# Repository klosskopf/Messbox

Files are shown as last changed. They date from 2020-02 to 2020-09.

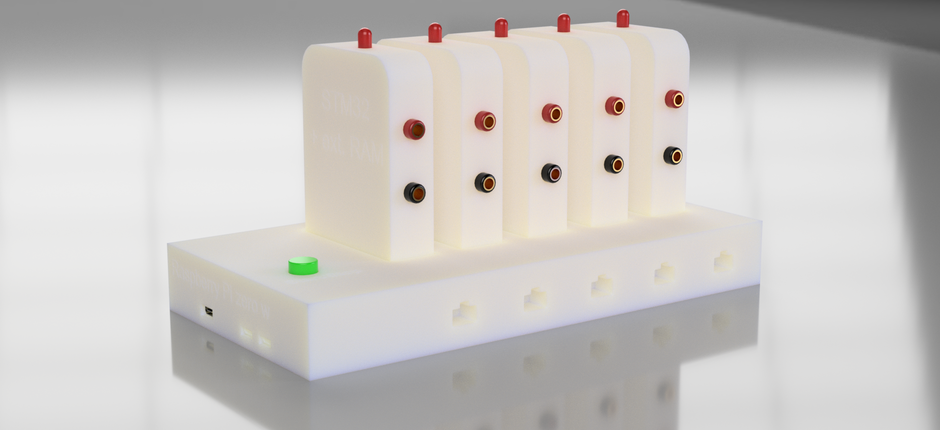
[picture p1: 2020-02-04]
doc/Messbox_Render.png

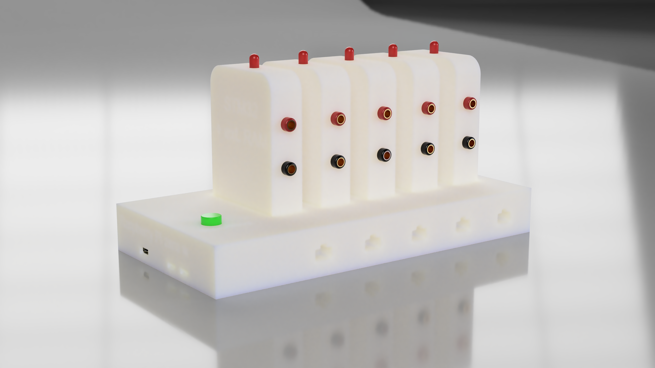
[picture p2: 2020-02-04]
doc/Messbox_Render_2K.png

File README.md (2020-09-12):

Dieses Repository beinhaltet alle Dateien zum Projekt Messbox 2000

Im Ordner *Raspberry* befindet sich der QT 5.11.3 C++ Code für die Middleware und Kennlinienerzeugung
Die Software muss mit root-Rechten ausgeführt werden. Damit die Aplikation ein Gui anzeigen kann,  
muss ```export XAUTHORITY=/home/pi/.Xauthority``` an /etc/profiles angehängt werden.

Im Ordner *Basisplatine* findet sich der Schaltplan und Layout für die Basisplatine

Im Ordner *STM32* befindet sich der C Code für die STM32 uC

Im Ordner *Steckkarte* befindet sich der Schaltplan und Layout für die Steckkarte.

Im Ordner *ATMEGA88* befindet sich der C Code für den atmega88 zur Erzeugung der sample frequenz und allgemeines

Im Ordner *BOM* finden sich Stücklisten und Bestellungsinfos für JLCPCB

Im Ordner *doc* finden sich alle Schemata, die das System beschreiben

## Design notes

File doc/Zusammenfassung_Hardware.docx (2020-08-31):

# Basisplatine-Hardware

Die Basisplatine übernimmt im Wesentlichen die Aufgaben eines Mainboards. Sie dient als Verbindungsglied zwischen Raspberry Pi und den einzelnen Steckkarten. Sie versorgt die Elemente mit allen nötigen Resourcen, wie 5V und 3,3V Spannungsversorgung und dem synchronen Sampletakt, der von einem Atmega88 Mikrocontroller erzeugt wird.

## Spannungsversorgung

Um einen möglichst großen Eingangsspannungsbereich nutzen zu können, besteht die erste Stufe der Spannungswandler-Schaltung aus einem Buck-Converter, der Spannungen zwischen 6V und 25V effizient auf 5V wandelt. Somit kann der Nutzer sich frei für eine Spannungsquelle entscheiden, solange diese mindestens 5W liefern kann. Denkbar sind beispielsweise 9V, 12V oder 15V Netzteile, aber auch mobile Lösungen, wie 2S, 3S, oder 4S Li-Ion Akkus, sollte die Betriebsdauer des integrierten Akkus nicht ausreichen. Wenn eine externe Spannungsversorgung angeschlossen ist, wird der interne Akku mit ca. 0,5A geladen. Verbaut ist eine 18650 Li-Ion Zelle mit 2000mAh. Mit dieser Zelle kann die Messbox bis zu einer Stunde ohne externe Stromversorgung betrieben werden. Um im Netzbetrieb den Akku laden zu können, wird das System in diesem Fall ganz über die bisher erzeugten 5V betrieben und nicht über die Batteriespannung. Gelöst wird dies durch zwei als OR verschaltete Shotkey –Dioden. Um die, um die Diodenspannung gesunkene, Spannung beziehungsweise die Batteriespannung wieder auf die benötigten 5V zu bekommen, folgt nun noch ein Boost-Converter. Um etwaige Rippel/Spitzen aus dem Rest der Schaltung zu halten, folgt nun noch ein LC-Filter. Mit diesen 5V werden der RaspberryPi und die Steckkarten versorgt, die nach der galvanischen Trennung daraus selbst 3,3V für die CMOS basierte Logik zu erzeugen. Auch der Raspberry selbst benötigt eigentlich 3,3V für seinen SOC, diese werden jedoch auf dem Einplatinenrechner selbst erzeugt. Diese werden auch durch den GPIO-Header in die Baisplatine eingespeist und versorgen hier den ATMEGA88. Der AVR könnte zwar auch mit 5V betrieben werden, durch die 3,3V sparen wir uns jedoch die sonst nötigen Pegelwandler für den SPI-Bus. Obwohl die Steckkarten sich ihre 3,3V selbst erzeugen, bekommen diese auch die 3,3V des Raspberry Pi. Damit wird jedoch lediglich das Chip-Select-Signal mit einem Pull-Up versorgt.

## SPI-Bus

Die Kommunikation des Raspberry-Pi mit den Steckkarten und dem ATMEGA88 erfolgt über einen einzigen SPI-Bus. Dieser befindet sich in einer Multi-Slave Konfiguration. Der Raspberry kann frei entscheiden, an wen er alles gleichzeitig Daten schicken möchte. In diesem Fall gibt es Pakete, die an alle Slaves, nur einen Karte, oder nur den ATMEGA88 gehen. Sinniger Weise darf immer nur ein Slave antworten. Um bei der Kommunikation mit mehreren Slaves keinen Kurzschluss zu verursachen, sind die MISO-Signale als open-drain Konfiguriert, wobei sich ein gemeinsamer Pull-Up auf der Basisplatine befindet. Weil ein SPI-Bus sehr empfindlich auf Übersprechen der Datenleitungen auf den Takt reagiert, wurde hierauf besonderes Augenmerk gelegt. Zum einen ist der SPI-Takt getrennt von anderen Datenleitungen gelayoutet und durch Masseflächen Abgeschirmt. Zum anderen sind alle Signale mit 100Ohm Serienterminiert und auf ca. 100Ohm Impedanz dimensioniert.

## ATMEGA88

Die Hauptaufgabe des ATMEGA88 besteht darin, einen exakten Sampletakt bereitzustellen. Dazu teilt dieser einen 12MHz Quarztakt durch einen Peripherie-Timer herunter und gibt das erzeugte Signal direkt in Hardware auch aus. Die Software des ATMEGA88 dient lediglich als Slave am SPI-Bus und konfiguriert die Hardware. Da dadurch noch genügend Resourcen auf dem Mikrocontroller frei sind, übernimmt dieser zusätzlich noch die Kontrolle der Spannungsversorgung. Die gesammelten Daten können über ein GET_STATUS Paket abgefragt werden, finden in der Software jedoch noch keine Verwendung.

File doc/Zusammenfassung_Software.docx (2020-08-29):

# Benutzeroberfläche

Um die Entwicklung und Bedienung so einfach wie möglich zu gestalten, finden sich alle Bedienelemente und der Graph auf einer Oberfläche, die bei Start des Systems gestartet wird.

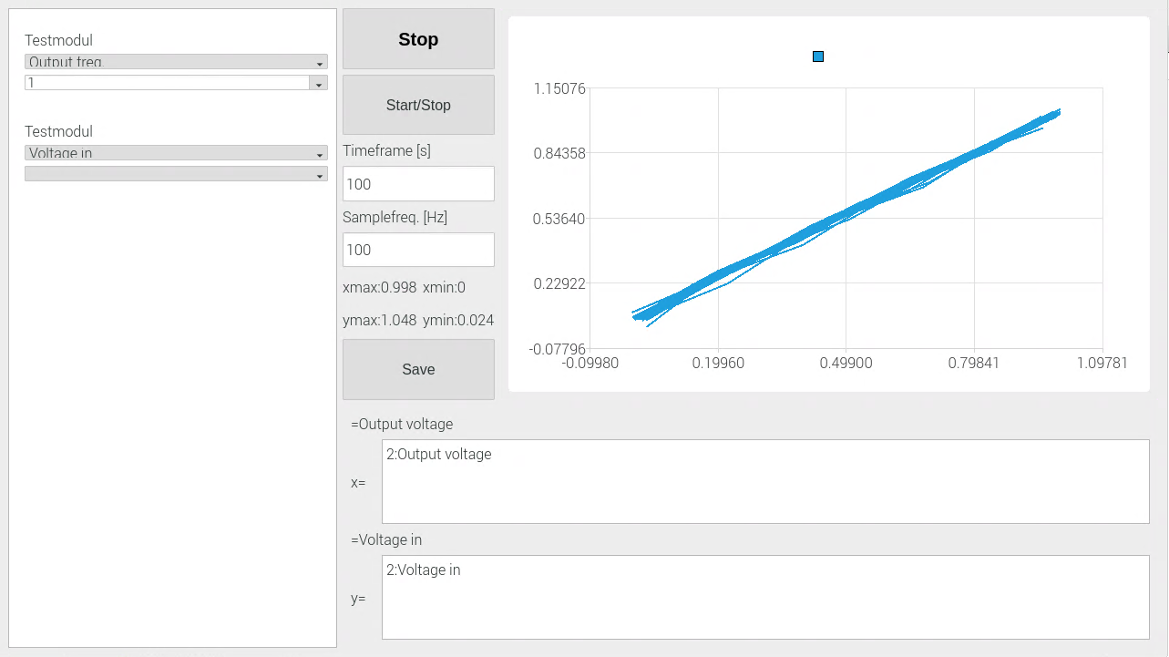
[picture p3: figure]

Die einzelnen Elemente Skalieren mit unterschiedlichen Monitorauflösungen in gleichem Umfang, benötigen allerdings eine Mindestauflösung von 405 x 543 Pixel, wobei die Oberfläche dann nur noch sehr eingeschränkt nutzbar ist. Im linken Abschnitt werden die eingesteckten Karten angezeigt. Schwebt die Maus über einer Karte, wird der Slot angezeigt, den die Karte belegt. Die Zählweise beginnt bei 1 im Slot ganz links. Die RJ45 Buchsen erhalten die Nummern 6-10. Eine dargestellte Karte besteht aus dem Kartennamen, einer Auswahlbox, die die einzelnen Parameter der Karte beinhaltet und einer Werte-Auswahlbox. Wird ein Parameter ausgewählt, wird das Werte-Dropdown Menü angepasst. Je nachdem, ob der Parameter frei anpassbar ist, nur aus einer Liste ausgewählt werden kann, oder gar nicht geändert werden kann. Im obigen Fall besitzt das erste Testmodul einen Parameter “Output freq.“, der frei änderbar ist. Zusätzlich kann aber auch aus einer Liste ein vorgeschlagener Wert übernommen werden. Beim zweiten Testmodul ist der Parameter „Voltage in“ ausgewählt. Dieser Parameter kann nicht geändert werden, sondern dient lediglich als Datenlieferant. Die Karte übermittelt zu Beginn ihren Namen und alle Parameter an die Basisstation. Unter anderem auch die Schreib-Rechte und Wahlmöglichkeiten der einzelnen Parameter.

In der Mitte finden sich die Kontrollelemente. Der erste Button ist eine Kopie des physischen Buttons. Mit diesem kann eine Messung gestartet und gestoppt werden. Findet gerade eine Messung statt, wird „misst…“ angezeigt, ansonsten „Stop“.
Mit dem zweiten Button wird der Messmodus gewechselt. Verfügbar sind „Start/Stop“, in dem eine feste Zeit lang gemessen wird, und „Cont.“, wohinter der Kontinuierliche Mess-Modus steckt. Wird der Modus während einer Messung gewechselt so werden alle bisherigen Werte verworfen und die Messung neu gestartet.
Die Zeitdauer, die im Graph angezeigt wird, kann im Feld „Timeframe“ stufenlos eingestellt werden. Im Start/Stop-Modus entspricht diese der Messdauer. Auch die Sample-Frequenz kann stufenlos eingestellt werden. Hardwarelimitiert sind dabei Werte zwischen 0.1Hz bis 10kHz wählbar, wobei alles über 1kHz aufgrund fehlender Zuverlässigkeit vermieden werden sollte.
Weil es zuweilen recht mühsam ist, Werte aus dem Graphen auszulesen, werden zumindest die aktuellen Minimal und Maximalwerte des sichtbaren Graphen für beide Achsen angezeigt.
Mit dem „Save“-Button können alle erfassten Parameter des Messsystems in „.csv“-Dateien gespeichert werden. In diesem Prozess wird zunächst die aktuelle Messung gestoppt und dann alle Parameter aller Karten restlos ausgelesen. Abhängig von der Anzahl an Karten, Parameter und Messdauer kann das eine Weile in Anspruch nehmen. Im Anschluss wird der Benutzer aufgefordert einen Speicherort für die Dateien auszuwählen. Dies geschieht in einem Dateiexplorer, sodass auch angeschlossene Speichermedien gewählt werden können, wenn diese ein Linux-Kompatibles Dateisystem besitzen (z.B Fat32). In dem ausgewählten Verzeichnis wird eine Ordnerstruktur erstellet. Gekapselt unter einem Ordner mit dem aktuellen Datum und Uhrzeit wird für jede Karte ein eigener Ordner erstellt, der für die einzelnen Parameter eigene „.csv“-Dateien erstellt. So muss der Nutzer in der Auswertung nicht alle Parameter in Excel laden, sondern kann sich nur die genutzten auswählen. Gespeichert wird für jeden Parameter die Zeit in Sekunden und der Messwert.

Welche Messwerte, wie im Graphen dargestellt werden, wird mit den beiden Formeln dargestellt. Hier können für die x-Achse und y-Achse unabhängig mathematische Formeln angegeben werden. Im dargestellten Bespiel wurde der x-Achse der Spannungsausgang der Testkarte aus Slot 2 zugewiesen und der y-Achse der Spannungseingang derselben Karte. Im Testaufbau wurden lediglich die beiden Bananenbuchsen miteinander verbunden. Zuvor wurde der Spannungsausgang mithilfe der Parameter „Output min.“, „Output max.“ und „Output freq“ so konfiguriert, dass eine Dreieckspannung mit 1Hz zwischen 0V und 1V ausgegeben wird. Da viel Karten denselben Namen haben, in unserem Fall zweimal „Testkarte“, muss ein Parameter über seinen Kartenslot und Parameternamen angesprochen werden. „2:Voltage in“ referenziert also den Parameter „Voltage in“ der Karte in Slot 2. Sollte es diesen Parameter nicht geben, wird eine entsprechende Fehlermeldung ausgegeben. Das manuelle Eingeben der Parameter kann umgangen werden, indem die Karte mit ausgewähltem Parameter per Drag and Drop in den Formeleditor gezogen wird. Parameter können auch mit mathematischen Operatoren miteinander kombiniert werden. Zur Verfügung stehen + - * / ( ) D S.
„D“ bildet dabei die Ableitung einer nachstehenden Klammer und „S“ das Integral. Auch Gleitkommazahlen sind erlaubt. Soll auch die verstrichene Zeit in die Achse mit eingehen, so kann der Operator „T“ verwendet werden.

Die dadurch festgelegte Messreihe wird im Graphen dargestellt. Die Achsen skalieren dabei automatisch mit. Befindet sich die Messung im kontinuierlichen Modus, werden alle Messwerte aus dem festgelegten letzten Zeitraum angezeigt. Der Nutzer ist selbst verantwortlich, das System nicht mit der Menge der anzuzeigenden Messwerte zu überfordern. Ein guter Richtwert sind 1000 Messpunkte. Bei mehr als 10000 Messpunkte droht eine Überlastung der CPU und dem Freeze der Benutzeroberfläche. Im Start/Stop-Modus gibt es diese Limitierung nicht. Hier wird nur eine Auswahl der Messwerte angezeigt, sodass die maximale Anzahl in dieser Messung die 1000 nicht überschreitet. Gespeichert werden in beiden Modi aber alle Messwerte, ob sichtbar oder nicht.

# Aufbau der Raspberry Pi Software

## Threads

Die Software des Raspberry Pis ist darauf ausgelegt, den SPI Bus maximal auszulasten. Es soll vermieden werden, dass der Raspberry Pi keine Daten abfragen kann, und somit den Buffer der Steckkarten unnötig strapaziert, nur weil die Daten gerade ausgewertet werden. Es muss auch verhindert werden, dass das Lesen und Decodieren eines besonders langen Pakets Benutzereingaben verzögert. Die von uns gewählte Lösung besteht aus der Aufteilung in mehrere Threads. Das ermöglicht auch den Wechsel von einem Einkern-Systems, wie dem ursprünglich vorgesehenen Raspberry Pi Zero, auf ein Multicore System, wie den Raspberry Pi, der zusätzlich mit weitaus größerem Arbeitsspeicher ausgestattet ist, was die maximale Aufnahmedauer stark erweitert.

Die Threads laufen je eine Endlosschleife, wobei die Synchronisation durch verschieden Maßnahmen gewährleistet bleibt. Die Software besteht aus folgenden fünf Threads:

## Post-Thread:

Der Postthread ist für die Spi-Kommunikation mit den Steckkarten zuständig. Da diese dauerhaft ausgelastet sein soll, bleibt dieser auch immer aktiv. Seine Aufgabe besteht darin, Pakete aus einer queue zu lesen und entsprechend des Protokolls mit Daten zu füllen. Die eigentliche Low-Level Übertragung wird mittels der wiringPi – Bibliothek durchgeführt. Diese nutzt DMA Transfers, wodurch Rechenzeit für andere Tasks frei wird. Wurde ein Paket fertig gesendet und simultan empfangen, so wird es an den Decoder- Thread weitergeleitet, der dieses nun Zeitunkritisch bearbeiten kann. Um Race-Conditions ausschließen zu können, genügt es, lediglich die Queue und Chip-Select-GPIOs mittels Mutex-Semaphoren zu schützen. Um ein korrektes Abarbeiten der Pakete zu gewährleisten, reicht es, das Abfragen der Queue-Größe, sowie das Entnehmen eines Paketes zu schützen. Die Chip-Select-Leitungen werden zusätzlich vom Control-Thread zur Erkennung von neuen Karten benötigt. Diese müssen also auch mithilfe einer Mutex-Semaphore vor gleichzeitigem Zugriff geschützt werden. Die Suche nach neuen Karten wird lediglich selten und sehr schnell abgearbeitet und fällt daher nicht wirklich ins Gewicht. Manche Pakete, wie GET_DATEN und GET_PARAMETER besitzen keine feste Länge. Diese wird von der Steckkarte vorgegeben und wird in den ersten Bytes übermittelt. Für ein Paket sind in diesem Fall also zwei DMA Transfers notwendig. Der Thread ist in sich in einem Modul geschlossen, und bietet eine API zum Hinzufügen von neuen Paketen.

## Decoder-Thread

Nachdem das Paket empfangen wurde, können die Daten zeit-unkritisch ausgewertet werden. Weil die empfangenen Daten eine zu schützende Ressource darstellen, kann es im decode-Schritt zu Wartezeiten kommen, die die SPI-Kommunikation nicht aufhalten sollen. Aus diesem Grund benötigt auch der Decoder-Thread eine Warteschlange, die vom Postthread gefüllt wird. Hier kann es jedoch zu Zeiten kommen, in denen keine Pakete zum Auswerten bereit sind. In diesen Zeiten soll der Thread nicht ins busy-wait laufen, sondern Schlafen. Die Synchronisation wird hier durch eine condition-variable gelöst, die den Thread nur dann aufweckt, wenn er gerade schläft. Der Decoderer erkennt selbstständig die Art des Pakets und speist die erhaltenen Daten in den Rest des Systems ein.

## Control-Thread:

Gefüttert wird der Post-Thread durch den Control-Thread. Dieser ist in dem control-Modul beheimatet, das zentral den Zustand des Systems leitet. Die Aufgabe des Control-Threads ist es, neue Karten zu finden und nach Parameteren zu fragen, sowie die Daten zu besorgen, die gerade für den Graph benötigt werden. Die Bandbreite des SPI-Buses, limitiert durch das SPI-Modul des STM32, erlaubt es nicht, von allen Karten ständig alle Parameter-Daten abzufragen. Weil die Liste mit momentan gebrauchten Parametern jedoch vor der Grapherstellung geschützt werden muss, ist es sinnvoll, nur für das Befüllen der Post-queue diesen eigenen Thread zu verwenden.

## Graph-Thread:

Der Graphthread ist lediglich ein Relikt aus vergangenen Versuchen, der nun lediglich eine Funktion im Haupt-Thread aktviert, die neue Datenpunkte in den Graph lädt. Diese Funktion soll in einem weiteren Refaktoring-Schritt durch einen QTimer ersetzt werden.

## Haupt-Thread:

Im Hauptthread werden die Qt-Objekte verwaltet. Also die Gui-Elemente. Dazu zählen insbesondere die dynamische Anzeige der Karten, das Parsen der Achsen-Gleichungen und Anzeigen des Graphen. Weil ein Gui Element in Qt nur im Hauptthread erzeugt werden kann, die neue Karte jedoch im Decoder-Thread erzeugt wird, besteht eine Karte aus zwei Objekten. Das eine für den Zugriff auf die Karte mit Parameterliste und einem Gui-Teil. Durch Erzeugen der Karte im Decode-Thread wird ein Signal an den haupt-Thread gesandt, der dann den zugehörigen Gui-Teil erstellt.
Als besonders Leistungshungrig hat sich das Erstellen des Graphen herausgestellt. Ein Graph in Qt besteht aus einem Graph, einem View-Objekt, das die Darstellung übernimmt und Serien, die die Datenpunkte besitzen. Zunächst wurde versucht, einzelne Datenpunkte aus der Serie zu löschen und neue Anzuhängen. Wie sich herausstellte, ist das eine sehr ineffiziente Möglichkeit. Besser ist es, die gesamte Serie mit neuen Datenpunkten zu befüllen (series->replace()). Dabei wird ein Zwischenspeicher benötigt, der gesamt in die Serie übernommen wird. Dazu wird zunächst festgestellt, zu welchem spät möglichsten Zeitpunkt alle Parameter über Daten verfügen. Befindet sich die Messbox im Kontinuierlichen Modus, so werden nun die nicht mehr benötigten Datenpunkte aus dem Zwischenspeicher gelöscht. Und dann neue Datenpunkte bis zum vorher bestimmten Zeitpunkt hinzugefügt. Nun können die Datenpunkte der Serie ausgetauscht werden. Was bleibt ist das Problem, dass die Achsen des Graphs, und damit auch der Anzeigebereich, eingestellt werden muss. Und dazu wird der minimale und maximale Wert des aktuell sichtbaren Bereichs benötigt. Ein stupides Durchgehen des Zwischenspeichers ist jedoch nur bei geringen Datenmengen durchführbar und wird daher auch nur im Kontinuierlichen Modus angewandt. Im Start-Stop-Modus wird beim Hinzufügen des Datenpunkts der minimale und maximale Wert aktualisiert. Weil bei langen Zeitdauern, wie sie spezifiziert sind, die Performance massiv beeinflusst würde, wenn mit jedem Zeitpunkt alle Datenpunkte neu gezeichnet werden würden, werden die angezeigten Datenpunkte in diesem Modus auf 1000 begrenzt. Es werden natürlich auch die dazwischen liegenden, nicht angezeigten Punkte mit abgespeichert.
Festgelegt, welche Parameter auf welcher Achse angezeigt werden, wird durch Auswertung der Achsen-Formeln. Die sich daraus ergebende Struktur wird aktualisiert im Fall einer neuen Eingabe, oder auch bei Einfügen und Ausstecken einer Karte. Die Formeln werden zunächst in die einzelnen Komponenten geparst, um Parameter von Zahlen und Rechenoperationen unterscheiden zu können. In einem weiteren Schritt werden nun die Elemente in die richtige Topologie gebracht. Gelöst wird dies rekursiv durch Prioritäten der einzelnen Elemente. Um den neuesten Zeitpunkt zu erhalten, oder einen Wert für einen Zeitpunkt zu bekommen, muss lediglich die entsprechende Funktion in der Wurzel aufgerufen werden, die dann rekursiv weiterläuft und die Rechenoperationen anwendet. Obwohl die Daten nur in single precision float Qualität erhoben werden, erfolgt die Berechnung und Darstellung im double Zahlenbereich. Das sichert auch bei großen Zahlen die erforderliche Genauigkeit in den Berechnungen.

# Programmablauf

Nun soll beschrieben werden, wie das Programm funktioniert. Das Programm wird ständig versuchen, den Graph zu erstellen. Weil die Datenpunkte des Graphen ja nicht beständig neu gesucht werden, führen bestimmte Aktionen, wie das Eingeben eines neuen Zeitfenster oder Achsenformel zu einem Löschen des Graphen, wodurch dieser einmalig wieder komplett neu erstellt wird. Es ist ersichtlich, dass das Erstellen des Graphen völlig von den anderen Aktivitäten unabhängig ist. Das hat den Nachteil, dass die Daten und der Datenbehälter vor gleichzeitigem Zugriff geschützt werden müssen. Insbesondere muss das Programm davor geschützt werden, Daten von einem Parameter zu erfragen, den es schon gar nicht mehr gibt. Das kann vorkommen, wenn während des Erstellens des Graphen eine Karte ausgesteckt wird, oder sich die Achsenbelegung ändert. Gelöst wurde das Problem durch eine große Mutex-Semaphore, die sowohl die Graph Erstellung, als auch den Achsen-Formel-Parser und das Löschen einer Karte klammert. Da zwei der drei verwendeten Stellen nur sehr selten vom Benutzer ausgeführt werden, ist die Performanceeinbuße hinnehmbar.

Damit der Control-Thread weiß, welche Daten gerade benötigt werden, hält der Parser eine Liste an Parameter-Pointern bereit. Der Control-Thread wird nun beständig versuchen, die queue des Post-Thread mit 10 Paketen gefüllt zu halten. Dadurch können jederzeit Status, Parameter und Befehle gesendet werden und der Rest der SPI-Kapazität wird im Round Robin Verfahren mit Datenanfragen gefüllt. Auch das Abfragen nach Daten ist unabhängig vom Zustand des Systems. Das ermöglicht es, Auch nach abgeschlossener Messung, den Graph mit anderen Parametern zu belegen. Diese werden dann so schnell wie möglich aus dem Zwischenspeicher der Steckkarten ausgelesen. Nachdem der Decoder die Daten ausgelesen hat, stehen sie im System zur Verfügung, bis eine neue Messung gestartet wird. Dann werden die Daten sämtlicher Parameter gelöscht und die Steckkarten setzen ihren Zwischenspeicher zurück. Intern liegen die Datenpunkte in einem vector gespeichert in den Parametern. Das hat den Vorteil zu einer verketteten Liste, dass die Daten auch mit einem Index angesprochen werden können. So muss nicht jedes Mal die gesamte Liste bis zum gesuchten Zeitpunkt abgesucht werden. Stattdessen merkt sich der Parameter den zuletzt verwendeten Index. Es ist nun sehr wahrscheinlich, dass bei erneutem Aufruf derselbe(doppelte Verwendung des Parameters) oder nächste Datenpunkt gesucht wird. Auch wenn Datenpunkte in der Anzeige übersprungen werden, wie es im Start-Stop-Modus der Fall ist, lässt sich so die Graph Erstellung bedeutend beschleunigen.

# Protokoll

Um den Datenaustausch maximal effizient zu gestalten, setzen wir auf unser eigenes Daten und Kommando Protokoll. Die Verwendung einer Einheitlichen JSON – Form wurde zwar in Betracht gezogen, letztendlich wollten wir allerdings die Möglichkeit sowohl float-Daten binär, als auch ascii-Parameter, ohne viel overhead versenden zu können. Die übertragung erfolgt in Little-Endian, da sowohl STM32, als auch Raspberry Pi auf Little-Endian Arm Architekturen bestehen. Das erleichtert die Umwandlung von empfangenen Bytes in float-Variablen ungemein. Es sind bisher 8 Befehle definiert, wobei das Protokoll Platz für 256 bieten würde.

## GET_PARAMETER: 0x01 : An einzelne Karte

Erkennt der Control-Thread eine neue Karte, sendet er ein GET_PARAMETER Paket an den entsprechenden Slot. Mit diesem Paket wird der Name der Karte erfragt und welche Parameter die Karte bietet. Ein Parameter besteht dabei aus einer Nummer, die künftig zur Identifikation im SET_PARAMETER und GET_DATEN Paket dient, einem Parameternamen, mit dem der Benutzer interagiert, minimal und maximal Werten und einer optionalen Werteauswahl. Die einzelnen Angaben sind immer nur durch ein Zeichen getrennt. Die Paket-Länge bezieht sich auf die Byte-Zahl des Parameter-Teils

| Befehl | Paket-Länge | Parameter
MOSI | 0x01
MISO | | 0-20000 | Kartenname,Parameternummer,Name,Typ,Parametrierbar,Min,Max{Wahl1,Wahl2,…}Parameternummer,…

uint8_t uint32_t ascii

Befehl | 0x01 für GET_PARAMETER
Paket-Länge | Byte-Zahl der Parameter
Kartenname | Wird dem Benutzer in der Kartenübersicht angezeigt. Intern verwendet wird jedoch ausschließlich der Index des Slots, in den die Karte gesteckt ist. Es können also auch zwei gleichnamige Karten eingesteckt sein.
Parameternummer | Nummer unter der der Parameter in weiteren Befehlen erreichbar ist
Parametername | Der Name des Parameters wird zusammen mit dem Kartenindex verwendet, um Parameter auf Achsen zuzuweisen
Typ | {s / f} : string oder float. Entscheidet, ob Daten vom Parameter abgefragt werden können und im Graphen dargestellt werden können. String Parameter können zum konfigurieren des Systems genutzt werden.
Parametrierbar | {l /f / n} : Liste, Frei, oder Nicht. Entscheidet, ob und wie der Benutzer den Parameter ändern kann. Liste: Der Benutzer kann keine freien Eingaben machen, aber aus den vorgegebenen Wahlmöglichkeiten wählen. Frei: Der Benutzer kann freie Eingaben machen, die zwischen min und max liegen müssen, sind Wahlmöglichkeiten vorhanden, so werden diese auch als drop down-Menü angezeigt. Nicht: Der Benutzer kann den Parameter nicht verändern. Er dient lediglich als Datenlieferant
Min | Der Minimalwert, der eingestellt werden kann. Muss immer angegeben werden; Wird als ASCII übertragen
Max | Der Maximalwert, der eingestellt werden kann. Muss immer angegeben werden.; Wird als ASCII übertragen
Wahl | Optional: Die Wahlmöglichkeiten, die dem Benutzer angezeigt werden. Werden im geschweiften Klammern angegeben. Falls keine Wahlmöglichkeiten vorhanden sind, folgt der nächste Parameter ohne Klammern mit einem Komma. Alle Wahlmöglichleiten werden als ASCII übertragen.

Wenn die Karte noch nicht bereit ist und nicht antwortet, so wird das Paket im Decoder als Fehlerhaft erkannt und keine neue Karte erstellt. Der Control-Thread wird im nächsten Versuch die Karte wieder als neu erkennen und einen neuen Versuch starten.

## SET_PARAMETER: 0x02 : An einzelne Karte

Ändert einen Parameter in der Karte. Der Parameter wird durch seine Nummer angesprochen. Es werden lediglich ASCII-Werte übertragen. Diese müssen eventuell in der Karte umgewandelt werden. Die Paket-Länge beinhaltet die 4 Byte der Parameternummer und die Länge des ASCII Parameterwert.

| Befehl | Paket-Länge | Parameternummer | Parameterwert
MOSI | 0x02 | 4 - 2^32 | 0 – 2^32
MISO | | | | Parameterwert

uint8_t uint32_t ascii

Befehl | 0x02 für SET_PARAMETER
Paket-Länge | Die Paket-Länge setzt sich zusammen aus 4 + Bytezahl des Parameterwerts
Parameternummer | Eindeutige Zuordnung des Parameters innerhalb der Karte
Parameterwert | Der Wert, auf den der Parameter gesetzt werden soll. Ist immer als ASCII codiert und wird bei Bedarf in der Karte umgewandelt. (atof())

## GET_DATEN: 0x03 : An einzelne Karte

Fordert Daten von einem Parameter an. Um den Bus nicht zu verstopfen und fehlerhafte Pakete ansatzweise zu erkennen, ist die Paketgröße auf 5000 Bytes softwareseitig begrenzt. Es ist ratsam, nur einzelne Pages des Zwischenspeichers auf einmal zu übertragen, um genug Zeit zu haben, neue Daten in das RAM zu laden. Ein Paket besteht dabei aus einer Anfangszeit und fortlaufenden Werten. Die Zeit bezieht sich dabei auf die Samples und nicht die eigentlich vergangene Zeit. Die Umwandlung erfolgt erst bei der Grapherstellung.

| Befehl | Parameternummer | Paket-Länge | Startzeit | Daten
MOSI | 0x03 | 0 - 2^32
MISO | | | 0-5000 | 0-2^32 | Datum1,Datum2,…

uint8_t uint32_t float

Befehl | 0x03 für GET_DATEN
Parameternummer | Damit die Karte angeben kann, wie viele Daten bereit sind, braucht sie den Parameter, um den es geht.
Paket-Länge | Die Paket-Länge entspricht nur der Länge des Daten-Teils. Also Anzahl an Datenpunkten * 4
Startzeit | Die Sample-Zeit des ersten Datums. Folgende Daten erhalten inkrementell entsprechende Sample-Zeiten
Daten | Die übertragenen Werte als float in Little Endian

## START_KONT: 0x04 : An alle Karten und ATMEGA88

Alle Daten löschen alle Zwischenspeicher und der ATMEGA88 beginnt den Sample-Takt. Nicht abgefragte Daten werden bei vollem Zwischenspeicher überschrieben.

| Befehl
MOSI | 0x04
MISO

## START_STARTSTOP: 0x05 : An alle Karten und ATMEGA88

Alle Daten löschen alle Zwischenspeicher und der ATMEGA88 beginnt den Sample-Takt. Nicht abgefragte Daten werden bei vollem Zwischenspeicher nicht überschrieben, sondern neue Daten verworfen.

| Befehl
MOSI | 0x05
MISO

## STOP: 0x06 : An alle Karten und ATMEGA88

Der ATMEGA88 beendet den Sample-Takt.

| Befehl
MOSI | 0x06
MISO

## SET_SAMPLE_FREQ : 0x07 : An alle Karten und ATMEGA88

Setzt die Sample Frequenz des ATMEGA88 auf einen neuen Wert. Wird aber erst bei START_KONT, oder START_STARTSTOP gestartet.

| Befehl | Frequenz
MOSI | 0x07 | 0.1-10000
MISO

uint8_t float

Befehl | 0x02 für SET_PARAMETER
Frequenz | Die Frequenz, die der ATMEGA88 als Sample-Frequenz erzeugen soll

## GET_STATUS: 0x08 : Nur an ATMEGA88

Frägt die Betriebsspannungen der Basis ab. Der Raspberry Pi besitzt keinen ADC, also wird hierfür der ATMEGA88 genutzt.

| Befehl | 5V | 3,3V | Ladestrom | Vbat | Vint | Vin
MOSI | 0x08
MISO | | 5.0 | 3.30 | 0.0 – 0.5 | 4.20 | 5.0 | 6.0 – 25.0

uint8_t float

Befehl | 0x08 für GET_STATUS
5V | Die 5V Spannungsversorgung, die entgültig den Raspberry Pi und die Steckkarten speist.
3,3V | Der 3,3V Ausgang des Raspberry für die CPU des Raspberry Pi, den ATMEGA88 und die Pull-Ups der Chip Select Leitungen
Ladestrom | Der momentane Ladestrom des Lithium-Ionen Akkus
Vbat | Die aktuelle Spannung des Akkus
Vint | Die Basisplatine wandelt die Eingangsspannung in eine Zwischenspannung von 5V um, mit der der Akku geladen wird.
Vin | Der Eingangs Buck-Converter erlaubt eine Eingangsspannung zwischen 6 und 25V

# Interessante Programmabschnitte

## Kartenerkennung

Um GPIO-Pins zu sparen, erfolgt die Erkennung neuer Karten durch die Chip-Select Leitungen. Der Raspberry aktiviert hierzu die 50k Pull-Downs auf den Chip-Select Leitungen. Auf den Karten hingegen befinden sich auf diesen Leitungen 10k Pull-Ups. Wenn der Raspberry nun auf neue Karten prüft, schaltet er die Chip-Select-Leitungen auf INPUT. Wenn keine Karte gesteckt ist, wird der Low-Pegel des internen Pull-Downs gelesen, wenn die Karte jedoch gesteckt ist, kann der Pull-Up der Streckkarte den Pegel auf 2,75V ziehen, was im High-bereich des Raspberry Pi liegt. Der SPI-Slave der Steckkarte sieht dabei die gesamte Zeit ein inaktives HIGH-Signal. Soll mit der Karte kommuniziert werden, muss lediglich der GPIO wieder auf OUTPUT und LOW geschaltet werden.

## Formel-Parser

Um die einzelnen Rechenelemente aus der Achsenformel zu separieren, wurde ein Mealy Zustandsautomat verwendet. Die folgenden Zustände können eingenommen werden: START, KLAMMERAUF,KLAMMERZU,TIME,INTEGRATE,DERIVATE,ZAHL,PUNKT,PARAMETER,MINUS. Wenn ein unerlaubter Übergang auftritt, wird das Parsen abgebrochen und der Benutzer erhält eine rudimentäre Fehlernachricht.

### START:

Der Startzustand wird nur am Anfang angesprungen und erlaubt nur rechtsseitige Operatoren

Zeichen | Neue erkanntes Element | Nächster Zustand
( | Klammer auf | KLAMMERAUF
T/t | Zeit | TIME
S/s | Integral | INTEGRATE
D/d | Ableitung | DERIVATE
0-9 | | ZAHL
- | | MINUS
. | | PUNKT

### MINUS:

Der MINUS Zustand kennzeichnet eine negierte Zahl/Parameter. Kein Minus Operand, der Zwei Zahlen subtrahiert. Bzw. Die erste Zahl ist in diesem Zustand immer 0

Zeichen | Neue erkanntes Element | Nächster Zustand
( | Konstante 0, Minus, Klammer auf | KLAMMERAUF
T/t | Konstante 0, Minus, Zeit | TIME
S/s | Konstante 0, Minus, Integral | INTEGRATE
D/d | Konstante 0, Minus, Ableitung | DERIVATE
0-9 | | ZAHL
. | | PUNKT

### KLAMMERAUF:

In diesem Zustand befindet man ich nach einer geöffneten Klammer. Verhält sich wie START

Zeichen | Neue erkanntes Element | Nächster Zustand
( | Klammer auf | KLAMMERAUF
T/t | Zeit | TIME
S/s | Integral | INTEGRATE
D/d | Ableitung | DERIVATE
0-9 | | ZAHL
- | | MINUS

### KLAMMERZU:

In diesem Zustand befindet man ich nach einer geschlossenen Klammer. Bei manchen Übergängen kann sich ein „Mal“ gespart werden

Zeichen | Neue erkanntes Element | Nächster Zustand
+ | Plus | START
- | Minus | START
* | Mal | START
/ | Geteilt | START
( | Mal, Klammer auf | KLAMMERAUF
) | Klammer zu | KLAMMERZU
T/t | Mal, Zeit | TIME
S/s | Mal, Integral | INTEGRATE
D/d | Mal, Ableitung | DERIVATE
0-9 | Mal | ZAHL
. | Mal | PUNKT
/0 | | Fertig

### TIME:

Nach einem t/T kann man sich ein „Mal“ sparen, da es wie eine Variable gelesen wird

Zeichen | Neue erkanntes Element | Nächster Zustand
+ | Plus | START
- | Minus | START
* | Mal | START
/ | Geteilt | START
( | Mal, Klammer auf | KLAMMERAUF
) | Klammer zu | KLAMMERZU
T/t | Mal, Zeit | TIME
S/s | Mal, Integral | INTEGRATE
D/d | Mal, Ableitung | DERIVATE
0-9 | Mal | ZAHL
. | Mal | PUNKT
/0 | | Fertig

### INTEGRATE:

Für INTEGRATE wird ein weiterer Zustand benötigt, da die Topologie keine zwei Integrierer hintereinander schalten kann. Diese müssen durch Klammern getrennt werden.

Zeichen | Neue erkanntes Element | Nächster Zustand
( | Klammer auf | KLAMMERAUF
T/t | Zeit | TIME
. | | PUNKT
0-9 | | ZAHL
- | | MINUS

### DERIVATE:

Für DERIVATE wird ein weiterer Zustand benötigt, da die Topologie keine zwei Ableitungen hintereinander schalten kann. Diese müssen durch Klammern getrennt werden.

Zeichen | Neue erkanntes Element | Nächster Zustand
( | Klammer auf | KLAMMERAUF
T/t | Zeit | TIME
. | | PUNKT
0-9 | | ZAHL
- | | MINUS

### ZAHL:

In diesem Zustand befindet sich der Parser mitten in einer ganzen Zahl. Das kann sich zu einer Gleitkommazahl, zu einem Parameter entwickeln, oder eine ganze Konstante bleiben

Zeichen | Neue erkanntes Element | Nächster Zustand
+ | Konstante, Plus | START
- | Konstant, Minus | START
* | Konstante, Mal | START
/ | Konstante, Geteilt | START
( | Konstante, Mal, Klammer auf | KLAMMERAUF
) | Konstante, Klammer zu | KLAMMERZU
T/t | Konstante, Mal, Zeit | TIME
S/s | Konstante, Mal, Integral | INTEGRATE
D/d | Konstante, Mal, Ableitung | DERIVATE
0-9 | | ZAHL
. | | PUNKT
: | | PARAMETER
/0 | Konstante | Fertig

### PUNKT:

Nach einem „.“ kann nur noch eine Gleitkommazahl gemeint sein. Ein zweiter „.“ wäre nicht sinnvoll.

Zeichen | Neue erkanntes Element | Nächster Zustand
+ | Konstante, Plus | START
- | Konstante, Minus | START
* | Konstante, Mal | START
/ | Konstante, Geteilt | START
( | Konstante, Mal, Klammer auf | KLAMMERAUF
) | Konstante, Klammer zu | KLAMMERZU
T/t | Konstante, Mal, Zeit | TIME
S/s | Konstante, Mal, Integral | INTEGRATE
D/d | Konstante, Mal, Ableitung | DERIVATE
0-9 | | PUNKT
/0 | | Fertig

### Parameter:

Nach einem t/T kann man sich ein „Mal“ sparen, da es wie eine Variable gelesen wird

Zeichen | Neue erkanntes Element | Nächster Zustand
+ | Parameter, Plus | START
- | Parameter, Minus | START
* | Parameter, Mal | START
/ | Parameter, Geteilt | START
( | Parameter, Mal, Klammer auf | KLAMMERAUF
) | Parameter, Klammer zu | KLAMMERZU
/0 | | Fertig
else | | PARAMETER

Jetzt, nachdem die einzelnen Elemente der Formel getrennt wurden, müssen die Blöcke noch in die richtige Topologie gebracht werden. Zu diesem Zweck verfügt die Oberklasse „Rechenblock“ die rekursiv arbeitenden Funktionen „von_oben()“ und „von_unten()“. Eine Formel ist aufgebaut aus in sich geschachtelten Berechnungen. Es ist daher naheliegend, die Topologie der Formel als Baumstruktur nachzubilden. Und je nachdem, ob eine Berechnung gerade verlassen wurde, oder noch offen ist, muss der Baum verschieden erweitert werden. Gestartet wird der Baum zu Beginn an der Wurzel und ein Zeiger auf das zuletzt hinzugefügte Element wird zwischengespeichert. Bei diesem Rechenblock muss die rekursive Funktion fortgesetzt werden. Ob ein Rechenblock eine Berechnungsebene abschließt, oder eine neue startet, wird durch die Priorität der Blöcke festgelegt. Gestartet wird das Hinzufügen eines Rechenblocks durch aufrufen von „von_unten()“ des zuletzt hinzugefügten Elements. Zunächst wird geprüft, ob es sich bei dem hinzuzufügenden Element um eine schließende Klammer handelt, die gerade eine geöffnete Klammer schließt. Eine schließende Klammer hat die Eigenschaft, kein echter Rechenblock zu sein, sondern lediglich die Priorität der öffnenden klammer von 1 auf 5 (max.) zu erhöhen. Somit ist dieser Bereich für alle weiteren Blöcke nicht mehr erreichbar. Ist dem nicht der Fall, entscheiden die Prioritäten, wie es weiter geht. Ist die Priorität des neuen Block größer als die des aktuellen, oder es handelt sich um eine Klammer, wird der neue Block ein Eingang des aktuellen. Es kann nicht passieren, dass der Block von unten an einen anderen Block weitergegeben werden muss, weil ein einmal verlassener Bereich nicht wieder von unten aufgemacht werden kann. Wenn hingegen die Priorität gleich oder niedriger der des aktuellen Rechenblocks ist, wird die Entscheidung an die Ebene darunter über „von_oben()“ weitergegeben.

Dabei gibt die Funktion „von_oben()“ den Block so weit nach unten, bis die aktuelle Ebene eine niedrigere Priorität besitzt als die des hinzuzufügenden Rechenblocks. Dann wird der Block ein neuer Eingang dieser Ebene. Auch hier muss jedoch zunächst festgestellt werden, ob eine Ebene durch eine Klammer abgeschlossen wird und entsprechend die Priorität der Klammer erhöht werden. Es ist ersichtlich, dass Klammern durch das ändern Ihrer Priorität die Möglichkeit haben, Zweige mit niedrigen Prioritäten oberhalb von höherwertigen Zweigen anzusiedeln.

Die Prioritäten sind folgendermaßen gestaffelt:

0 : Achse

1 : offene Klammer

2: Plus, Minus

3: Mal, Geteilt

4: Integrate, Derivate

5: Zeit, Konstante, Parameter, geschlossene Klammer

-1: schließende Klammer (Wird nicht eingebaut, sondern macht offene Klammer zu geschlossener)

Um neue Funktionalität hinzuzufügen, muss der Zustandsautomat um die entsprechenden Übergänge ergänzt werden und ein neuer von „Rechenblock“ abgeleiteter Block definiert werden, der die Funktionalität in „get_data()“ implementiert und mit der richtigen Priorität ausgestattet ist. Möglicherweise müssen die Prioritäten dann neu geordnet werden.

# STM32 Software

Die Software des STM32 ist ausschließlich Interrupt basiert. Nach Initialisierung der Module, wird lediglich einmalig der SPI-Flash gelöscht und dann in der leeren main Schleife auf Interrupts gewartet. Die Software ist modular aufgebaut, sodass die Module einzeln entwickelt werden konnten und lediglich mit den richtigen Interrupt Prioritäten zusammenspielen müssen. Die Software besteht aus einem COM-Handler, Parametermodul, einem ADC Modul, einem DAC-Modul, einem Flash-HAL, einem GPIO-HAL und dem Hauptmodul, das noch einzelne Aufgaben erledigt, die zu klein für ein einzelnes Modul wären. Für viele der Aufgaben gäbe es auch von ST bereitgestellte HAL-Bibliotheken, jedoch sind diese enorm ineffizient und werden von uns dementsprechend ignoriert.

## GPIO-Modul

Um nicht jedes Mal, das Datenblatt des STM32 studieren zu müssen, wenn ein neuer Pin initialisiert werden soll, bietet unser Gpio-Modul eine init_gpio-Funktion, die alle wichtigen Parameter des Pins einstellen. So kann der Pin als Eingang, Ausgang, Analogpin, oder Alternate-Function (direkt mit Peripherie verbunden) initialisiert werden. Darüberhinaus können auch Pull-Up/Down, Slew-Rate und open Kollektor / Push-Pull Betrieb mit einem Funktionsaufruf eingestellt werden. Weiterhin werden Funktionen zum Lesen, Schreiben und Toggeln eines Pins bereitgestellt. Die meisten Pins sind jedoch direkt mit der Peripherie des STM32 verbunden.

## COM-Handler

Das COM-Handler-Modul besteht aus einer einzigen großen State-Maschine, die durch den SPI-Interrupt des mit dem Raspberry Verbundenen Peripheriemoduls ausgelöst wird. Um zuverlässig den Anfang und das Ende eines Pakets zu erkennen, wird das Chip-Select-Signal nicht nur zur Aktivierung des SPI-Moduls genutzt, sondern auch zum reseten der State-Maschine. Aus diesem Grund ist es notwendig, den Chip-Select Eingang mit einem Pin-Change-Interrupt zu belegen. In diesem Interrupt wird dann auch das SPI-Modul mittels Software Slave-Select aktiviert und deaktiviert.
Bei der Initialisierung dieses Moduls wird der Inhalt des GET_PARAMETER-Datensatzes aus der zuvor im Parameter-Modul gebildeten parameterliste gebildet. Das erlaubt das einfache Hinzufügen neuer Parameter, ohne an dieser Stelle etwas ändern zu können. Werden größere Datenmengen an den Raspberry Pi übertragen, wie etwa bei GET_PARAMETER oder GET_DATEN Paketen, so geschieht dies mittels DMA Transfers. So wird die Rechenlast auf die CPU minimal gehalten.

## Flash-Modul

Das Flash-Modul stellt Funktionen bereit, um mit dem 32/64/128Mbit SPI-Flash daten auszutauschen. Das Protokoll des Flash-ICs erlaubt dabei verschiedene Datenübertragungen. Es können entweder 4KByte, 32KByte, 64KByte, oder der ganze Chip gelöscht werden. Weil das Löschen selbst eines 4KByte Blocks jedoch mindestens 100ms, bis zu 400ms dauert, ist es uns nicht möglich das während des Betriebs zu tun. Die Option besteht jedoch für niedrige Sample-Frequenzen. In jedem Fall wird der gesamte Chip zu Beginn gelöscht, was bis zu 20-40 Sekunden benötigt. Die LED der Steckkarte signalisiert, wann die Karte einsatzbereit ist. Neue Daten können lediglich in 256Byte Blöcken geschrieben werden. Da bei so einer geringen Block-Größe allerdings ständig ausgelagert werden müsste und jede Menge Metadaten entstehen würden, wurde eine Block-Größe von 2KByte gewählt. Gelesen kann hingegen von jeder beliebigen Adresse mit voller SPI-Geschwindigkeit, ein beliebig großer Datenblock. Um das Paging zu vereinfachen werden jedoch auch beim Lesen immer exakt 2KByte gelesen.
Um nicht den gesamten Schreiben, oder Leseprozess im Programmablauf warten zu müssen, ist der gesamte Flash-HAL Interrupt basiert. Soll beispielsweise ein Block gelesen werden, um an den Raspberry geschickt zu werden, so wird das Modul in den Modus „Lesen“ versetzt und die Lesen-State-Maschine aufgerufen. Diese startet die Übertragung für das erste Byte and den Flash (In diesem Fall 0x0b, das „Fast Read“ Kommando) und gibt die Kontrolle bereits an das COM-Handler-Modul zurück, der die noch nicht eingetroffenen Daten an den Raspberry Pi leitet. Sobald das „Fast-Read“ Kommando gesendet wurde, wird der SPI-Interrupt ausgelöst. In der zugehörigen Interrupt Service Routine wird wieder die Lesen-State-Maschine aufgerufen, die die nächsten drei Male die Adresse an den SPI-Flash übertragt und dann ein Dummy Byte. Nun sind die Daten im Flash bereit an den STM32 übertragen zu werden. Um nicht bei jedem Byte extra einen Interrupt auslösen zu müssen und die State-Maschine aufzurufen, wird hierzu ein DMA-Transfer gestartet, der die Daten in einen Auslese-Buffer schreibt. Das macht es möglich, dass sich der Datenaustausch mit dem Raspberry Pi und dem Flash überlappen. In dem Moment, in dem der Raspberry bereits erste Daten erhält, wird noch der Rest der Daten aus dem Flash nachgeladen. Da der Flash mit seinen 10MHz weitaus schneller arbeitet als die Verbindung mit dem Raspberry Pi (1MHz), kann es nicht passieren, dass der Raspberry Daten liest, die noch nicht vom Flash befüllt wurden. Ist dieser DMA-Transfer abgeschlossen wird wieder ein Interrupt ausgelöst, die State-Maschine zurückgesetzt und das Flash-Modul für andere Operationen freigegeben. Auch die Lösch und Schreib-Operationen können völlig parallel zum Programmablauf und anderen Interrupts arbeiten.

## Parameter-Modul

Das parameter-Modul dient als Schnittstelle für die anderen Module. Ist ein neues Datum vorhanden, so kann dieses mit der „new_data()“-Funktion Eingespeist werden. Benötigt das COM-Handler Modul Daten eines Parameters, muss lediglich die „get_datenblock()“-Funktion genutzt werden, um bis zu einem Block an Daten zu erlangen. Das Modul übernimmt automatisch im Hintergrund anfallendes Paging und stellt ein Array aller Parameter bereit mit den zugehörigen Funktionen. Wenn ein neuer Parameter implementiert werden soll, muss lediglich der Name in eine entsprechende Enum-Variable eingetragen werden und der Parameter in der Parameterliste konfiguriert werden. Ein Parameter besteht dabei aus einem Strukt mit dem Typ „parameter_t“. Um einen Parameter zu parametrieren, benötigt er einen Namen, es muss festgelegt werden, ob es sich um einen im Graph darstellbaren Float-Parameter handelt, oder um einen nicht parametrierbaren String, der natürlich ebenfalls als Float dargestellt werden kann, von der Basis jedoch nicht in einer Formel verwendet werden kann. Auch die Schreibrechte des Parameters müssen festgelegt werden, sowie minimal und maximal-Werte. Machen min/max Werte keinen Sinn, muss dennoch ein Wert angegeben werden. Soll der Parameter Auswahlmöglichkeiten bereitstellen, muss ein string array als „wahl“ eingestellt werden. Wenn der Parameter im Graph angezeigt können werden soll, muss ein Zeiger auf ein Buffer-Element angegeben werden. Der Buffer und die Wahlmöglichkeiten müssen als Pointer übergeben sein und dann selbst definiert werden. Dieser Weg wurde gewählt, um möglichst Arbeitsspeicher zu sparen, da eine Karte signifikant viele String Parameter bietet, deren Buffer lediglich Speicher kosten würde, ohne genutzt zu werden. Das Buffer-Element besteht dabei aus drei 1 Block großen Buffern. Zwei Eingangsbuffern und einem Ausgangsbuffer. Um die Datenerfassung möglichst ohne weiteren Programmieraufwand erweitern zu können, kann gleich hier auch ein ADC-Channel des ADC1 eingetragen werden, sowie ein auf die Eingangsspannung anwendbarer Faktor und Offset. Soll der Parameter beschreibbar sein, muss auch noch ein Funktionspointer angegeben sein, dessen Funktion den empfangen String auswertet.

Wird ein neues Datum einem Parameter hinzugefügt und der aktive Eingangsbuffer ist voll, so wird der Startzeitpunkt des Blocks gesichert und der Eingangsbuffer wechselt, damit weiterhin neue Daten empfangen werden können. In regelmäßigen Abständen muss nun die Funktion „page_out_next()“ aufgerufen werden, die in allen Parametern nach einem so übergelaufenen Buffer sucht und bei jedem Aufruf nur einen Buffer durch den Flash-HAL auslagert. Dieses Verfahren wurde gewählt, weil mit hoher Wahrscheinlichkeit nicht nur ein Buffer, sondern alle Buffer überlaufen werden. Ein sofortiges Auslagern würde so länger als ein Sample Zyklus dauern und Daten verloren gehen. So wird die Last des Auslagerns von Blöcken über mehrere Sample-Zyklen verteilt. Um zu wissen, welcher Block im Flash mit welchem Parameter belegt ist, führt das Parametermodul eine Liste aller Blöcke, in der festgehalten ist, welcher Parameter den Block besetzt und bei welcher Startzeit der Block beginnt. Im Flash selbst sind somit lediglich die reinen Parameter-Werte gespeichert. Abhängig von dem verwendeten Flash-Chip und der eingestellten Block-Größe, nehmen selbst diese Meta-Daten einen beträchtlichen Speicherbereich in Besitz. Um das Finden eines neuen Speicherbereich möglichst performant zu gestalten und die Speicherzellen gleichmäßig zu belegen, merkt sich das Modul den zuletzt genutzten Speicherblock und versucht von da an nach neuem freiem Speicher. So kann auch ohne Löschen des Speichers maximal lang zuverlässig gemessen werden. Benötigt der COM-Handler Daten eines Parameters, wird zunächst in den gesamten Flash-Metadaten nach dem ältesten von diesem Parameter belegten Block gesucht. Diese Zeit muss die Basis mindestens von sich aus warten, bis Sie mit der Kommunikation fortfahren darf. Das entspricht ca. 1ms. Wird kein Block in den Flash-Metadaten gefunden, wird geprüft, ob gerade ein Block ausgelagert werden soll. In diesem Fall wird die Auslagerung abgebrochen und der volle Eingangsbuffer direkt an den COM-Handler übergeben. Ansonsten wird der gerade halb gefüllte aktive Eingangsbuffer übergeben, wobei dann eben kein ganzer Block übertragen wird. In Sachen Performance ist es enorm wichtig, dass die Daten in der chronologisch richtigen Reihenfolge an den Raspberry übertragen werden.

## Main-Modul

Wie bereits gesagt, beinhaltet die Main-Routine lediglich die Initialisierung des Systems und das Löschen des Flash-Speichers. Mit dazu gehört auch das anheben des System-Takts von 4MHz auf 80MHz durch einstellen der integrierten PLL. Da der interne Programmspeicher-Flash so schnellen Betrieb nicht unterstützt, mussten 2 Warte-Zyklen eingebaut werden, die die Abarbeitung des Programm-Codes bedeutend verlangsamen. Zusätzlich ist das Modul allerdings auch für das Abarbeiten eines Sample-events zuständig, dass über einen Pin-Change Interrupt ausgelöst wird. Dazu wird zum einen die ADC-Sequenz gestartet und alle nicht-ADC-basierten Parameter-Werte an das Parameter-Modul übergeben.

## ADC-Modul

Der STM32L431CBT6 verfügt über ein hoch komplexes ADC-Modul, von dem jedoch nur ein kleiner Teil genutzt wird. Das Peripheriemodul besitzt die Möglichkeit mit nur einem Trigger eine zuvor festgelegt Sequenz an ADC-Messungen durchzuführen. Diese Sequenz wird in der Initialisierung anhand der parameterliste gefüllt. Für jeden Kanal kann einzeln die Sample-Zeit eingestellt werden. Es wird standardmäßig für alle Kanäle 10us eingestellt. Jede Messung löst einen End of conversion ADC Interrupt aus, in dem der ADC-Wert gelesen wird, mit dem eingestellten Faktor und Offset verrechnet wird und an das Parameter-Modul übergeben. Ist die Sequenz fertig durchgelaufen, wird das auslagern eines Buffers ermöglicht, indem „page_out_next()“ des Parameter-Moduls aufgerufen wird. Der ADC bietet die Möglichkeit, Channels überabzutasten. Das wird auch genutzt und somit eine 16bit-Auflösung erzielt.

## DAC-Modul

Das Dac-Modul entspricht einem Beispiel einer Applikationssoftware. In diesem Fall wird ein Funktionsgenerator implementiert. Dieser hört auf die Parameter „Output max.“, „Output min“ und „Output freq.“. Es wird ein Dreiecksignal erzeugt, dass mit der gegebenen Frequenz zwischen den beiden Spannungen schwingt. Dazu wird ein extra Timer und das DAC-Modul des STM32 genutzt. Dieses bietet eine Auflösung von 12bit. Die momentan ideal ausgegebene Frequenz kann unter dem Parameter „Output voltage“ zur Grapherstellung genutzt werden.

# Hinzufügen eines Parameters

Einen neuen Parameter hinzuzufügen benötigt ein minimales Eingreifen ins System.

### „parameter.h“:

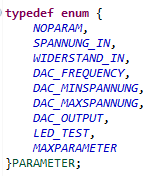
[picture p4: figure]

in parameter.h muss die intern verwendete Parameternummer in einer Enumerationsvariable definiert werden. Die somit eindeutig zugewiesene Nummer wird auch in der Basis zu Identifikation des Parameter verwendet. Der Eintrag muss dabei nach „NOPARAM“ und vor MAXPARAMETER erfolgen. Die Nummer NOPARAM=0 wird in den Metadaten des Flash-Speichers genutzt, um freie Speicherbereiche zu kennzeichnen. Mit MAXPARAMETER wird die Anzahl der Parameter ermittelt und dementsprechend die parameterliste dimensioniert.

### „parameter.c“:

Soll ein Parameter in der Grapherstellung genutzt werden, muss für ihn ein Buffer-Element bereitgestellt werden.

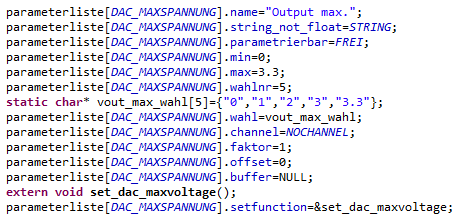
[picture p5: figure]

In der parameterliste muss der Parameter konfiguriert werden. Dazu gehören unter Umständen auch Wahlmöglichkeiten, Buffer und SET_PARAMETER Funktion.

### „adc.c“:

Weil aus den Nummern der ADC-Kanäle nicht der Pin hervorgeht, an den der Kanal verbunden ist, muss der Pin hier initialisiert werden. Dazu eignet sich der GPIO-HAL.

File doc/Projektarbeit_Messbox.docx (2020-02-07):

# Messbox 2000

Projekt 2020 von Timo Erdmannsdörfer und Johannes Wittmann

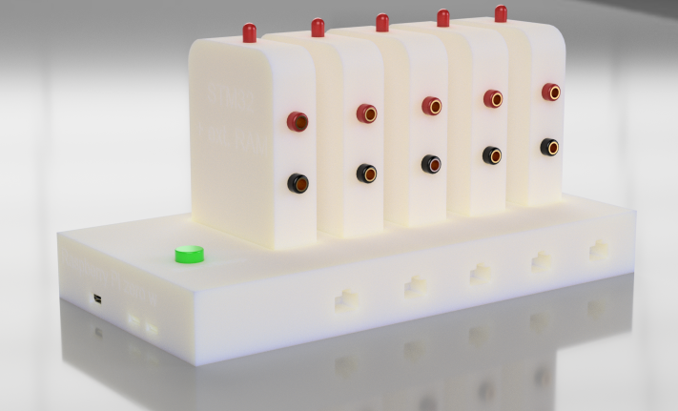
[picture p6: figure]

# 1. Zweck/Kernfunktionalität:

Die Messbox soll Messdaten(z.B Spannung, Temperatur) erfassen und diese graphisch anzeigen lassen können und abspeichern. Dabei soll diese ortsungebunden Messdaten aufnehmen können.

# 1. Mögliche Umsetzung:

# 1.1. Software:

Die graphische Anzeige wird über einen Pi(zero)(ca.20€) realisiert. Dieser hat usb für Maus und mini HDMI für einen Bildschirm.

Die zu erstellende Software auf dem pi soll Auswahl und Konfiguration der Messstationen über ein GUI und die graphische Anzeige der Messwerte ermöglichen.

Auch sollen die Messwerte und graphische Anzeige dieser abspeicherbar sein(png, csv).

Die Software hat mehrere Mess-Modi: kontinuierliche Messung, start-stop-Messung:

Kontinuierliche Messung: Anzeige der letzten aktuellen Daten, die vom pi empfangen wurden(überschreiben), Steckkarten übertragen Daten in Paketen. Bspw. werden die Messwerte der letzten 10s angezeigt. Maximale Buffergröße (z.B 10kS) als Ringbuffer. (Nach 10kS wird der erste Messwert gelöscht (Sonst würden nicht ausgelesene Werte immer mehr Speicher verbrauchen))

Start-Stop Messung: Start/Stop der Messung über Taster auf Platine, oder Zeitraum. Es werden alle Messwerte kontinuierlich gespeichert; So kann auch im Nachhinein entschieden werden, welcher Kanal ausgewertet werden soll. Ist der Buffer voll, werden keine weiteren Messwerte aufgenommen.

Zusätzlich könnte man über einen zweiten Button nachdenken, der alle Parameter der Karten ausliest und abspeichert, um absolut headless arbeiten zu können.

Die Software soll ermöglichen, die Daten miteinander zu verrechnen und anzuzeigen(z.B Differenzbildung/Multiplikation), wobei die Achsen automatisch skalieren. Ob das ohne Tastatur möglich ist, muss sich zeigen.

Die Samplefrequenz der Steckkarten soll schrittweise wählbar sein(z.B 1Hz, 100Hz, 1kHz, 10kHz).
Somit ist der Benutzer verantwortlich, den Messzeitraum geeignet zu wählen.

# 1.2. Basisstation:

Die Basisstation soll Platz für 5 Steckkartenplätze und 5 RJ12 Buchsen bieten, wobei über die RJ12 Buchsen analog zu den Steckkartenplätzen Steckkarten betreiben können sollen.

Die Software des Raspberry Pi soll in C++ geschrieben werden. Für die graphische Oberfläche soll QT verwendet werden.
Für QT gibt es ein Educational Programm. Dabei kann der Professor für die Studenten kostenfreie Vollversionen beziehen. (https://www.qt.io/qt-for-educational-program )

Die Kommunikation der Basistation(pi) mit Streckkarten soll über SPI erfolgen. Dabei hat jeder Steckplatz und jede RJ12 Buchse eine eigene Slave-Select Leitung, über die der Raspberry erkennt, ob eine Karte angeschlossen ist. (kein Gerät: leichter Pulldown, Gerät angesteckt: Pullup, Kommunikation: GPIO: LOW)

# 1.3. Messkarten:

Um die Messungen unabhängig voneinander durchführen zu können, sollen die Steckkarte galvanisch von der Basisstation getrennt sein.

Die galvanische Trennung der Kommunikation soll über Optokopler erfolgen, die sich auf der Steckkarte befinden.

Um eine flexible Einsetzbarkeit der Messbox zu gewährleisten, soll die Basisstation mit Steckkarten über Lithium-Ionen-Akkumulator betrieben werden(ACT2801QL-T1028). Das Laden dieser muss ebenfalls galvanisch getrennt erfolgen.

Der Akku der Basisstation soll über eine DC-Buchse geladen werden können. Angedacht ist eine oder mehrere Standard Li-Ionen Zelle.

Der Akku der Messkarte soll ebenfalls über die Basisstation geladen werden können. Es wird sich dabei vermutlich um 2023-Knopfzellen handeln.

Um die galvanische Trennung aufrecht zu erhalten, benötigt es hier einen galvanisch getrennten DC-DC-Konverter. Dieser befindet sich in der Basisstation

Nur eine Messkarte kann gleichzeitig geladen werden, um die galvanische Trennung unter den Karten aufrecht zu erhalten. So soll die Verbindung zur Basisplatine über ein Relais getrennt werden können.

Die Software für die Steckkarten wird in Standard C geschrieben

Die Gehäuse sollen in 3D-Druck erstellt werden

Für die Steckkarten soll als uC der STM32L431CB verwendet werden. Dieser bietet genug Schnittstellen für RAM, Kommunikation und Debugging, sowie eine FPU und zwei DACs, die zukünftig von Vorteil sein könnten.

Eine Status-LED ist in den Steckkarten zu verbauen, die anzeigt, wenn der Buffer der Karten voll ist. (im kontinuierlichen Modus, wenn in der letzten Übertragung der gesamte Buffer voll war; im Start/Stop Modus, wenn der gesamte RAM voll ist.)

Im Zuge des Projekts soll 1xSteckkarte für Spannungsmessung und 1xSteckkarte für Widerstandsmessung/Temperaturmessung aufgebaut werden.

# 2. Bussystem

# 3. Spannungsversorgung

# 4. Zeichnung

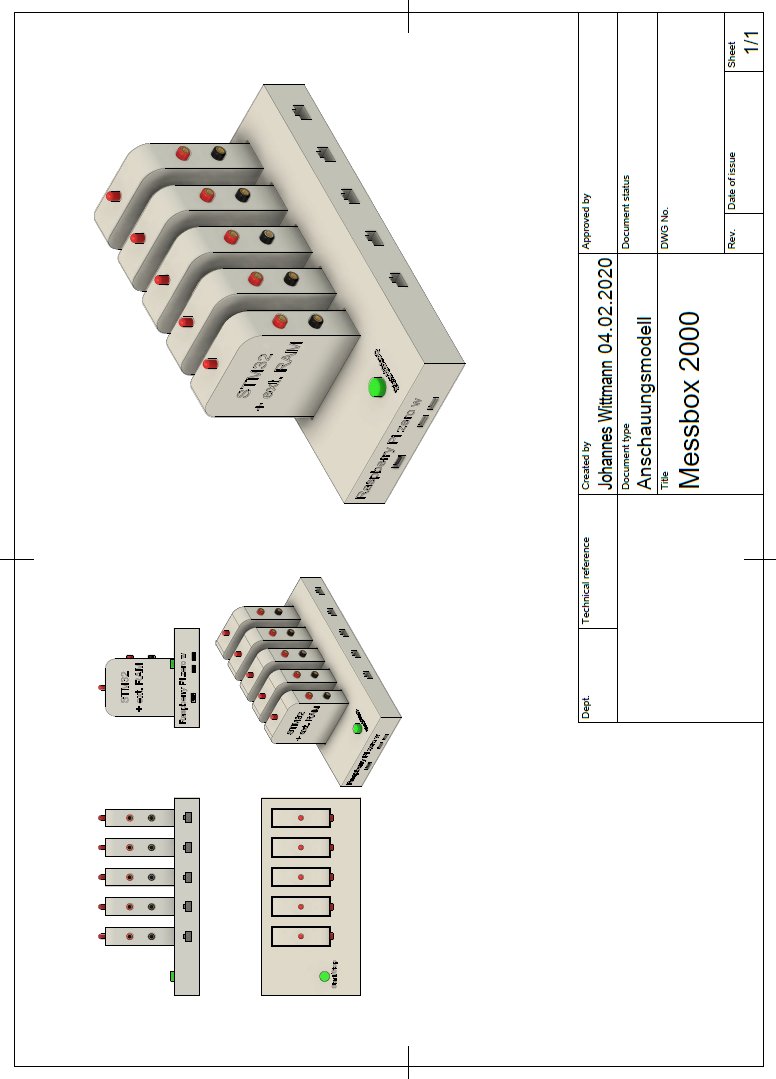
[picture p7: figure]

3Projekt 2020 – Timo Erdmannsdörfer / Johannes Wittmann05.02.2020

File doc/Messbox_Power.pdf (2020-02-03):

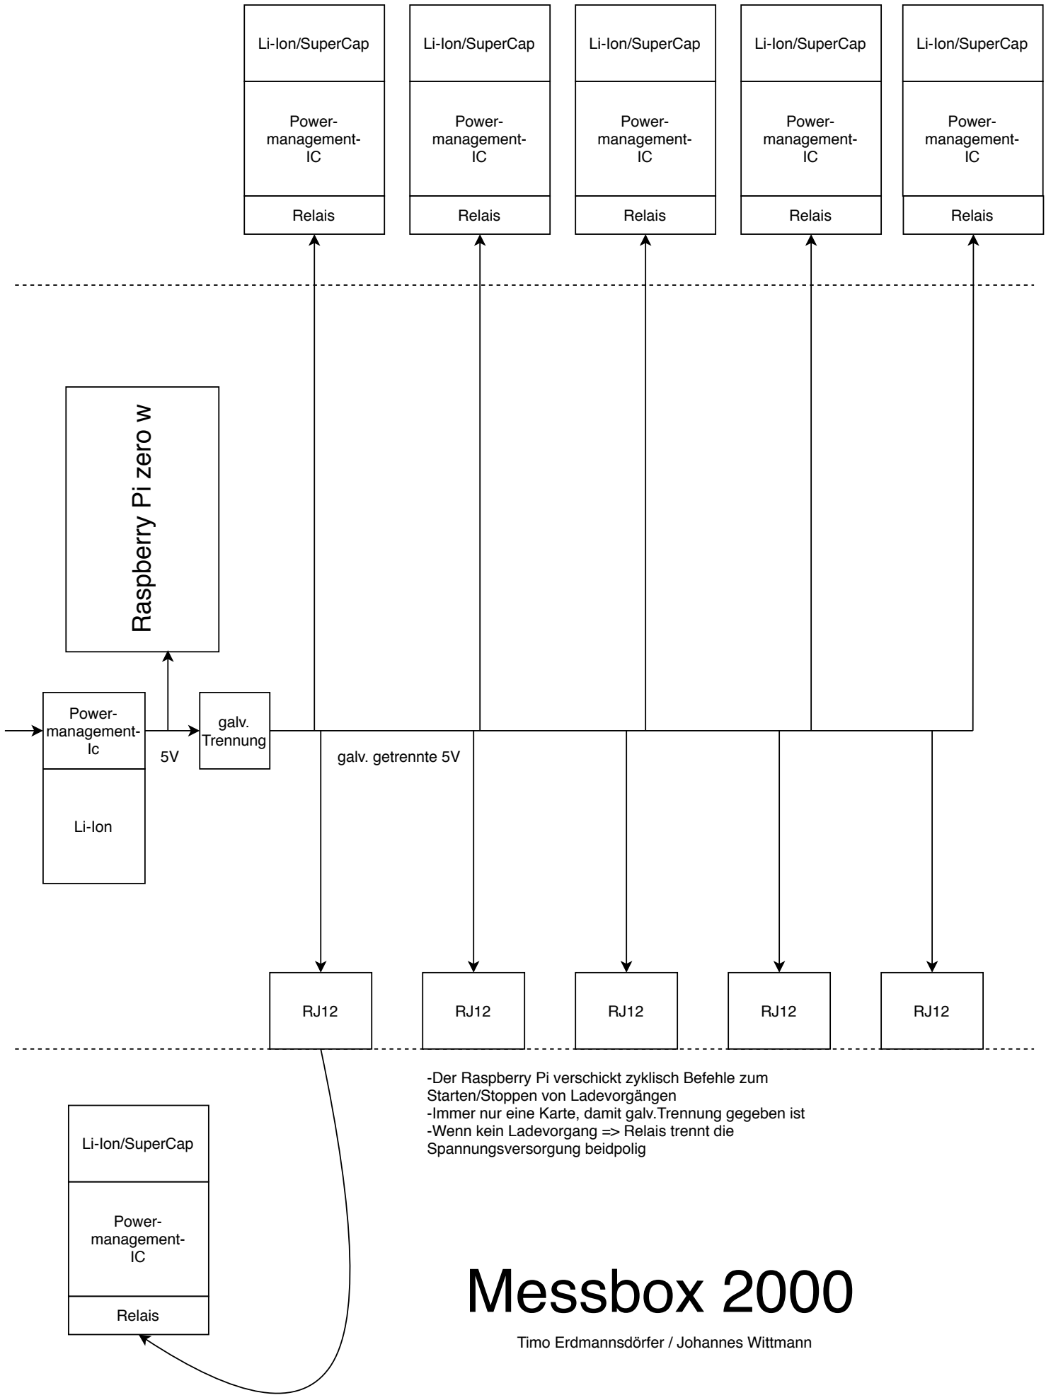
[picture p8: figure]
Raspberry Pi zero w; Power- management- IC; Relais; Li-Ion/SuperCap; Messbox 2000; Timo Erdmannsdörfer / Johannes Wittmann; Li-Ion; Power- management- Ic; galv. Trennung; galv. getrennte 5V; Starten/Stoppen von Ladevorgängen; Spannungsversorgung beidpolig

-Der Raspberry Pi verschickt zyklisch Befehle zum

-Immer nur eine Karte, damit galv.Trennung gegeben ist -Wenn kein Ladevorgang => Relais trennt die

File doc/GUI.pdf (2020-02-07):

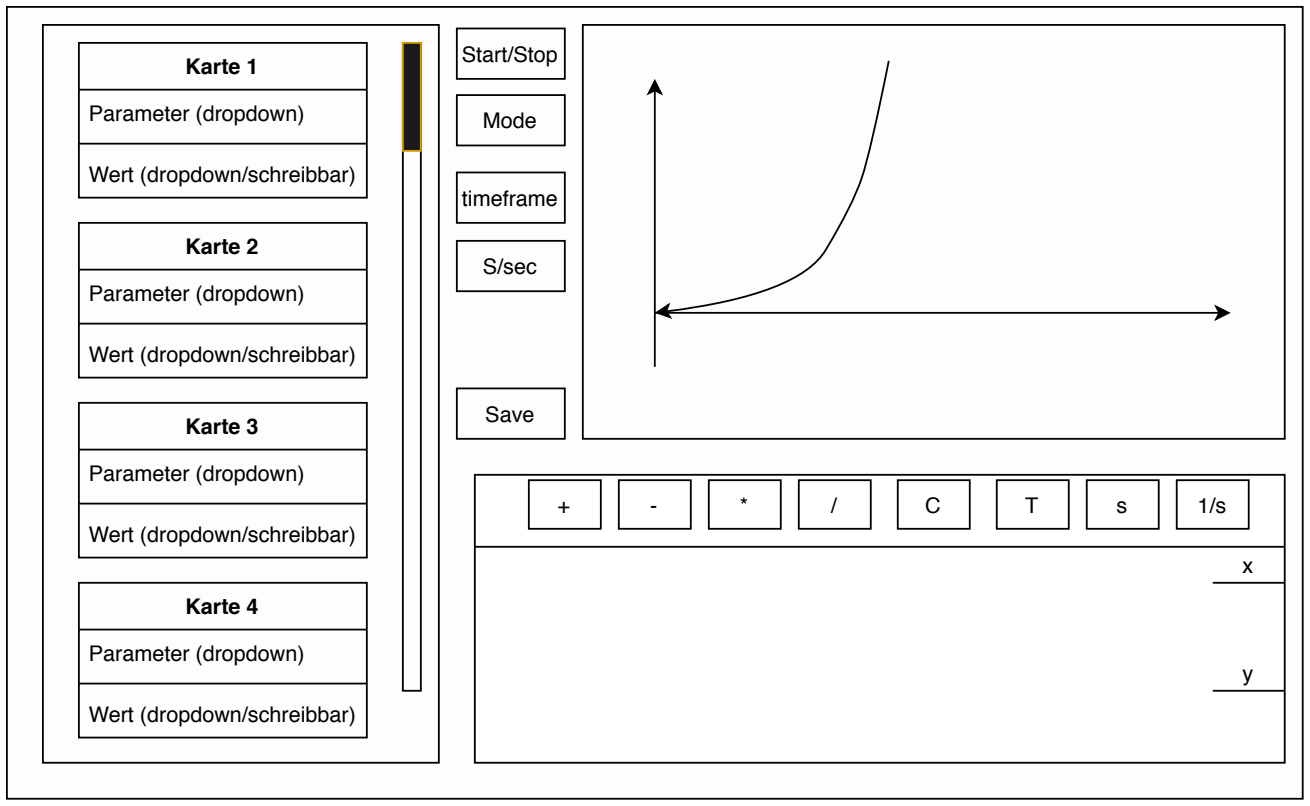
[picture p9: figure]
Karte 1; Parameter (dropdown) Wert (dropdown/schreibbar); Karte 2; Karte 3; Karte 4; Start/Stop; Mode; Save; timeframe; S/sec

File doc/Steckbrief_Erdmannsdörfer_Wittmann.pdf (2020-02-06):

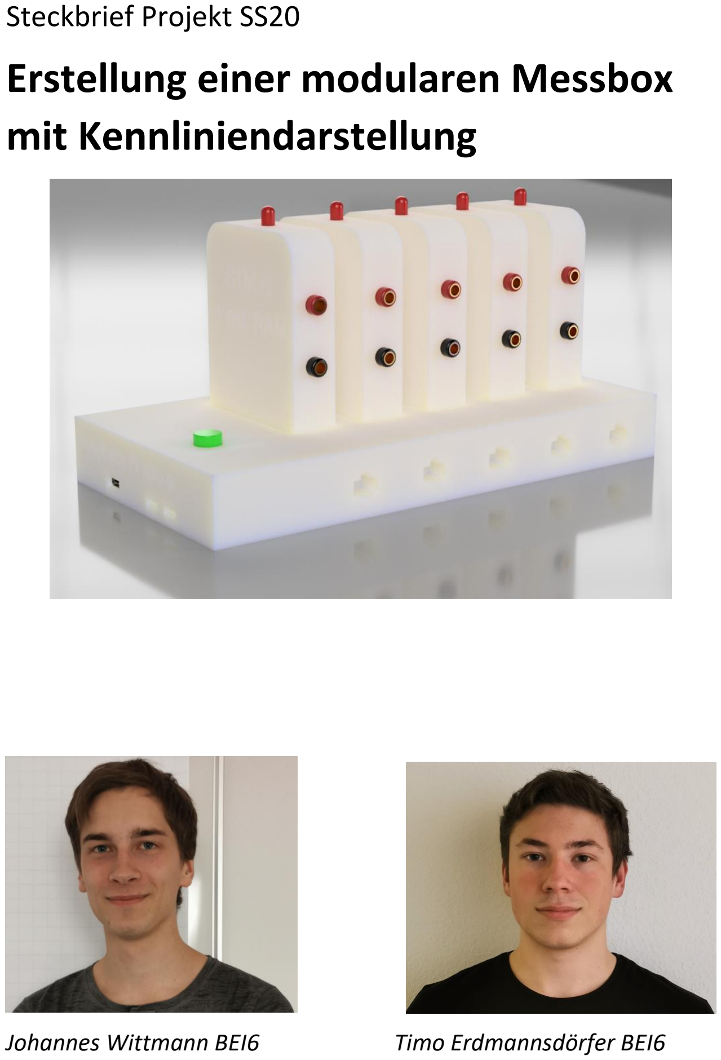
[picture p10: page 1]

Steckbrief Projekt SS20
Erstellung einer modularen Messbox mit Kennliniendarstellung
Johannes Wittmann BEI6 | Timo Erdmannsdörfer BEI6

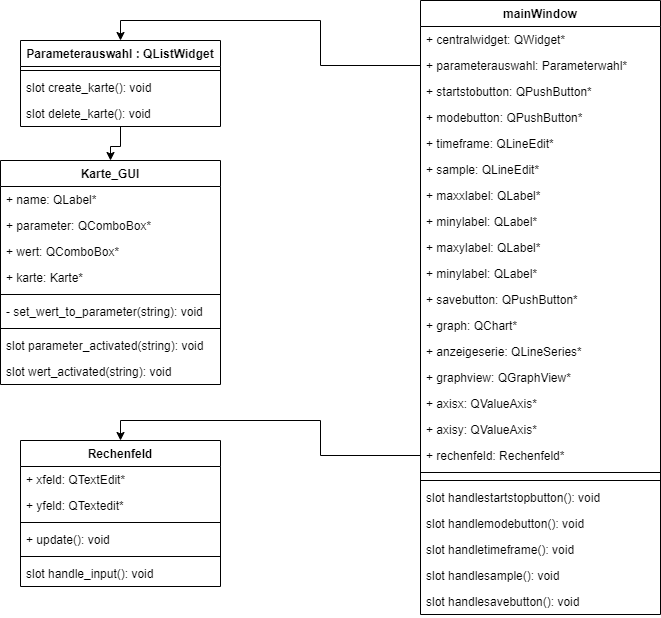
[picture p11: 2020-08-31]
doc/UML/uml_oberflaeche.png

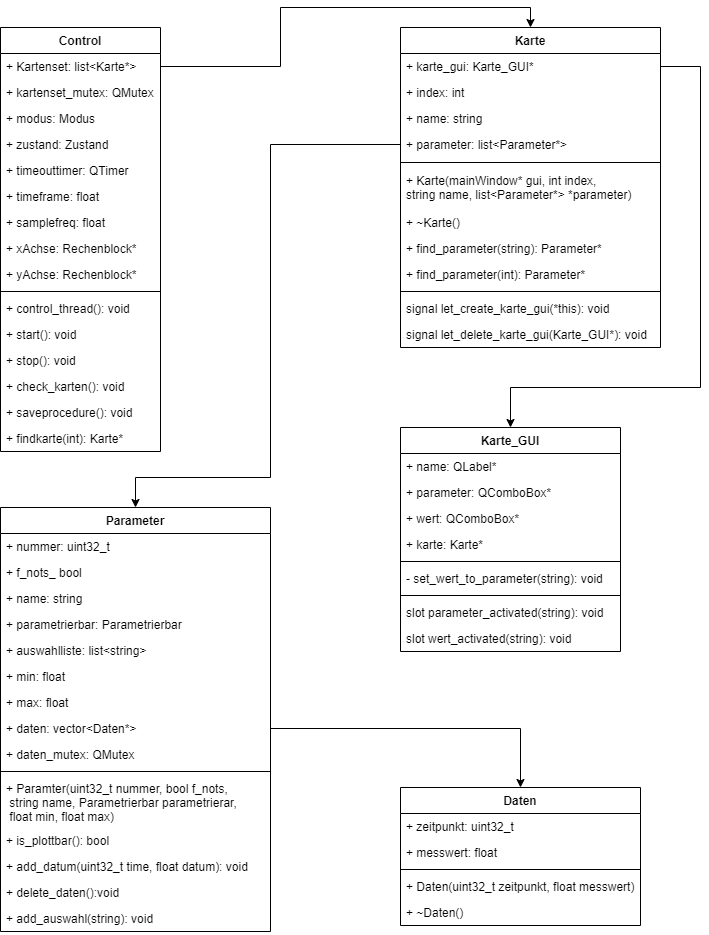
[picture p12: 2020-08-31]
doc/UML/uml_database.png

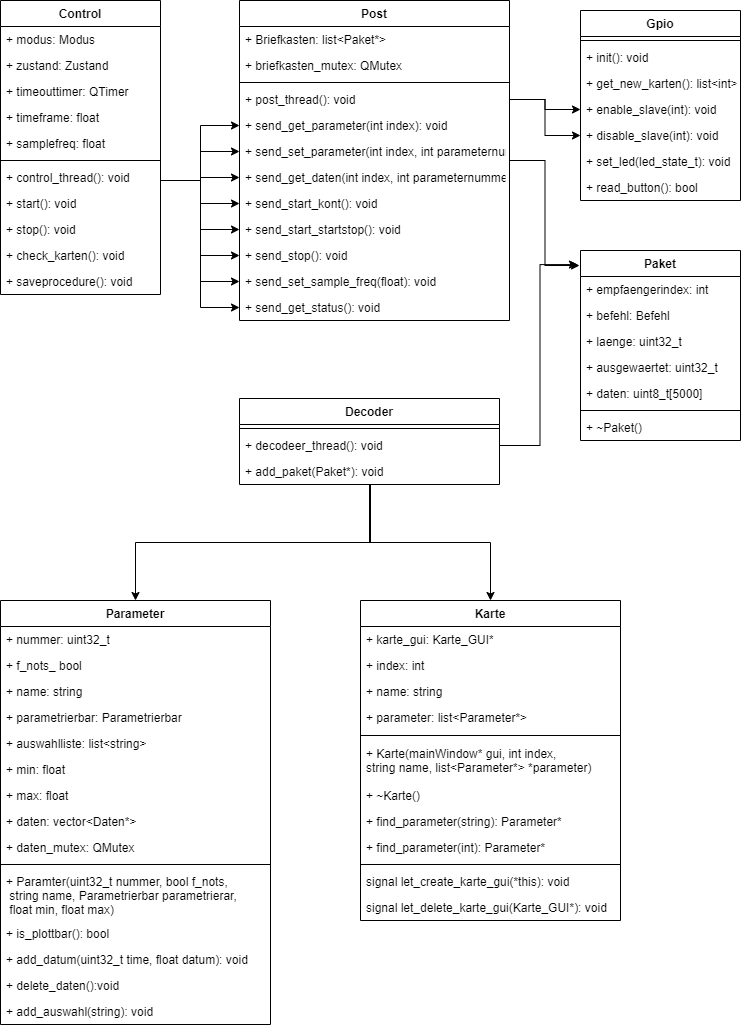
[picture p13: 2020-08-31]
doc/UML/uml_schnittstelle.png

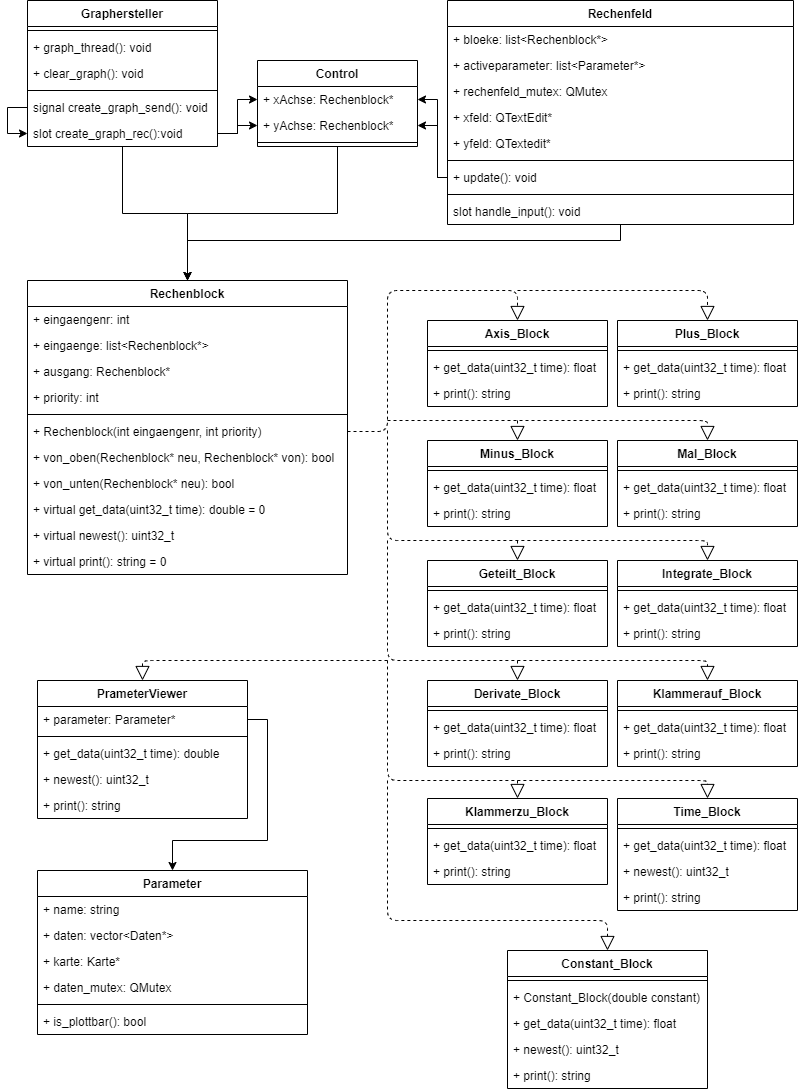
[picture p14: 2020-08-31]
doc/UML/uml_graphersteller.png

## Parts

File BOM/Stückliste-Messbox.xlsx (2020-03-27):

Bezeichnung | Shop | BestellNr. | Anzahl | Preis/Stück | Kosten
MLCC - SMD/SMT WCAP-CSGP 0.1uF 0603 10% 25V MLCC | Mouser | 710-885012206071 | 68 | 0.046 | 3.128 | Euro
MLCC - SMD/SMT WCAP-CSGP 0.01uF 0603 10% 25V MLCC | Mouser | 710-885012206065 | 3 | 0.1 | 0.3 | Euro
Keramikschichten MLCC - SMD/SMT 0603 16VDC 1uF 10% X5R | Mouser | 963-EMK107BJ105KA-T | 4 | 0.1 | 0.4 | Euro
MLCC - SMD/SMT 2.2uF 16V X5R +/-10% 0603 Gen Purp | Mouser | 963-EMK107BJ225KA-T | 6 | 0.13 | 0.78 | Euro
MLCC - SMD/SMT 0603 16V 4.7uF X6S 10% T: 0.8mm | Mouser | 810-C1608X6S1C475K | 16 | 0.12 | 1.92 | Euro
MLCC - SMD/SMT 0603 16V 6.8uF JB 10% T: 0.8mm | Mouser | 810-C1608JB1C685K08B | 3 | 0.6 | 1.8 | Euro
LM234DT | Mouser | 511-LM234D | 1 | 1.11 | 1.11 | Euro
OPA2333D | Mouser | 595-OPA2333AIDR | 1 | 3.5 | 3.5 | Euro
TLP2768A_TP,E | Mouser | 757-TLP2768ATPE | 3 | 1.44 | 4.32 | Euro
LED5MM | Mouser | 630-HLMP-4700 | 3 | 0.5 | 1.5 | Euro
Dünnfilmwiderstände - SMD 1/4W 5MOhm 0.1% AEC Q200 Qualified | Mouser | 754-RG3216P-5004B-T1 | 1 | 0.57 | 0.57 | Euro
Dünnfilmwiderstände - SMD 100 Kohm .1% 1206 25PPM | Mouser | 284-APC1206B100KN | 1 | 0.2 | 0.2 | Euro
Dünnfilmwiderstände - SMD 0603 120Kohm 1/10W AEC-Q200 | Mouser | 667-ERA-3AEB124V | 1 | 0.35 | 0.35 | Euro
Dünnfilmwiderstände - SMD 150mW 40kohm 0.1% 25PPM 0603 | Mouser | 71-PAT0603E4002BST1 | 1 | 0.75 | 0.75 | Euro
Dünnfilmwiderstände - SMD 20KOhm 0.1% 0603 25 PPM | Mouser | 284-APC0603B20K0N | 1 | 0.13 | 0.13 | Euro
hick Film Resistors - SMD 1/10Watt 10Kohms 5% Commercial Use | Mouser | 71-CRCW060310K0JNEBC | 4 | 0.1 | 0.4 | Euro
10k 0603 | Mouser | 754-RR0816P-103D | 27 | 0.09 | 2.43 | Euro
Dickfilmwiderstände - SMD 1/10Watt 499ohms 1% Commercial Use | Mouser | 71-CRCW0603499RFKEAC | 3 | 0.1 | 0.3 | Euro
Dickfilmwiderstände - SMD 0603 Anti-Surge Res. 0.1%, 470ohm | Mouser | 667-ERJ-PB3B4700V | 2 | 0.25 | 0.5 | Euro
Thick Film Resistors - SMD 160 OHM 1% | Mouser | 603-RC0603FR-07160RL | 15 | 0.018 | 0.27 | Euro
Dickfilmwiderstände - SMD 1/10Watt 22ohms 1% Commercial Use | Mouser | 71-CRCW060322R0FKEAC | 18 | 0.036 | 0.648 | Euro
EXB-N8V103JX | Mouser | 667-EXB-N8V103JX | 3 | 0.11 | 0.33 | Euro
Dickfilmwiderstände - SMD 1/10Watt 0ohms Commercial Use | Mouser | 71-CRCW06030000Z0EAC | 2 | 0.1 | 0.2 | Euro
VARISTOR B72660M0151K093 | Mouser | 871-B72660M0151K093 | 1 | 1.22 | 1.22 | Euro
STM32L412CBT6 | Mouser | 511-STM32L412CBT6 | 3 | 3.8 | 11.4 | Euro
LP5907QMFX-3.3Q1 | Mouser | 595-LP5907QMFX-3.3Q1 | 3 | 0.63 | 1.89 | Euro
RFM-0505S | Mouser | 919-RFM-0505S | 3 | 1.39 | 4.17 | Euro
INA317IDGKR | Mouser | 595-INA317IDGKR | 1 | 2.56 | 2.56 | Euro
TLV4110IDGNR | Mouser | 595-TLV4110IDGNR | 1 | 2.9 | 2.9 | Euro
W25Q64JVSSIQ | Mouser | 454-W25Q128JVSIQ | 3 | 1.4 | 4.2 | Euro
OPA333AIDBVR | Mouser | 595-OPA333AIDBVR | 1 | 2.46 | 2.46 | Euro
Lötstifte | Mouser | 534-680 | 25 | 0.2 | 5 | Euro
Industrial Temperature Sensors M222 Pt1000 Pt clad Ni- wire | Mouser | 956-32208571 | 1 | 3.12 | 3.12 | Euro
DIO5158XS8 | Mouser | 453-DIO5158XS8 | 2 | 0.58 | 1.16 | Euro
TPS613222ADBVR | Mouser | 595-TPS613222ADBVR | 2 | 0.92 | 1.84 | Euro
AP63205WU-7 | Mouser | 621-AP63205WU-7 | 2 | 0.94 | 1.88 | Euro
LFXTAL002996Bulk | Mouser | 449-LFXTAL002996BULK | 2 | 0.26 | 0.52 | Euro
NTF5P03T3G | Mouser | 863-NTF5P03T3G | 2 | 0.28 | 0.56 | Euro
BCW66HVL | Mouser | 771-BCW66HVL | 4 | 0.17 | 0.68 | Euro
SRN5040TA-4R7M | Mouser | 652-SRN5040TA-4R7M | 2 | 0.34 | 0.68 | Euro
SRP1038C-2R2M | Mouser | 652-SRP1038C-2R2M | 4 | 1.06 | 4.24 | Euro
SBRT10U50SP5-13 | Mouser | 621-SBRT10U50SP5-13 | 2 | 0.68 | 1.36 | Euro
SK33-TP | Mouser | 833-SK33-TP | 8 | 0.39 | 3.12 | Euro
5R 0603 | Mouser | 71-CRCW0603-4.99-E3 | 2 | 0.1 | 0.2 | Euro
100R 0603 | Mouser | 71-CRCW0603100RFKEAC | 34 | 0.026 | 0.884 | Euro
1k2 0603 | Mouser | 667-ERJ-3RBD1201V | 2 | 0.1 | 0.2 | Euro
2k 0603 | Mouser | 754-RR0816P-202D | 2 | 0.1 | 0.2 | Euro
82k 0603 | Mouser | 754-RR0816P-823D | 8 | 0.1 | 0.8 | Euro
270k 0603 | Mouser | 754-RR0816P-274D | 2 | 0.1 | 0.2 | Euro
DC-Jack | Mouser | 806-KLDX-0202-AC | 2 | 0.44 | 0.88 | Euro
RJ45-Buchse | Mouser | 649-54601-908WPLF | 5 | 0.54 | 2.7 | Euro
120pF 0603 | Mouser | 80-C0603C121J5GAC | 4 | 0.1 | 0.4 | Euro
10uF 1206 | Mouser | 581-1206DD106MAT2A | 16 | 0.232 | 3.712 | Euro
Raspberry Pi® Zero W / Scheint so gut wie überall ausverkauft; zur Not: selbst | Mercateo/selbst | 3272496006997 | 1 | 21.34 | 21.34 | Euro
Stiftleiste 2x10 | Conrad | 1560983 | 3 | 0.35 | 1.05 | Euro
Buchsenleiste 2x10 (BLG2X10) | Conrad | 1492267 - 62 | 10 | 0.32 | 3.2 | Euro
 |  |  |  | Summe: | 116.562 | Euro

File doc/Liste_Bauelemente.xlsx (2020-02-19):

LISTE BAUELEMENTE
Unterprojekt | Name Bauteil | Bezeichnung | Anmerkung | Händler | Bestellnummer | Preis/Stück | Anzahl | Anmerkung
Raspberry
Steckkarte | Flash | W25Q128JVSIQ
 | Miso-Optokoppler | TLP2768A(TP,E
 | SPI-Optokoppler | ACSL-6400-00TE
 | DC-DC-Wandler | RFM-0505S | 5V-5V
 | µC | STM32L431CBT6

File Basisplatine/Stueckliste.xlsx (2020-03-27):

Bauteil | Bezeichnung | Bauteil | Bestellnummer | Shop | Menge | Preis einzel | Preis
U1,U2,U3,U4,U5 | 20pin Stecker | BLG2X10 | 1492267 - 62 | Conrad | 5 | 0.32 | 1.6
IC1 | RaspberryPi 0 w | Raspberry Pi® Zero W | 3272496006997 | Mercateo | 1 | 21.34 | 21.34
IC3 | Laderegler | DIO5158XS8 | 453-DIO5158XS8 | Mouser | 1 | 0.58 | 0.58
IC4 | Boost-Converter | TPS613222ADBVR | 595-TPS613222ADBVR | Mouser | 1 | 0.92 | 0.92
IC5 | Buck-Converter | AP63205WU-7 | 621-AP63205WU-7 | Mouser | 1 | 1.31 | 1.31
Q1 | 32kHz Quarz | LFXTAL002996Bulk | 449-LFXTAL002996BULK | Mouser | 1 | 0.26 | 0.26
Q2 | discharge-Transistor | NTF5P03T3G | 863-NTF5P03T3G | Mouser | 1 | 0.28 | 0.28
T1,T2 | hold-on-transistor | BCW66HVL | 771-BCW66HVL | Mouser | 2 | 0.17 | 0.34
L1 | Buck-Spule | SRN5040TA-4R7M | 652-SRN5040TA-4R7M | Mouser | 1 | 0.34 | 0.34
U6,U8 | Boost-Spule | SRP1038C-2R2M | 652-SRP1038C-2R2M | Mouser | 2 | 1.06 | 2.12
U7 | Schottky-Diode | SBRT10U50SP5-13 | 621-SBRT10U50SP5-13 | Mouser | 1 | 0.61 | 0.61
U9,U10,U11,U12 | Schottky-Diode | SK33-TP | 833-SK33-TP | Mouser | 4 | 0.35 | 1.4
R15 | 5R 0603 | CRCW06034R99FKEA | 71-CRCW0603-4.99-E3 | Mouser | 1 | 0.1 | 0.1
R28,R26,R25,R24,R23,R22,R21,R20,R32,R37,R36,R35,R34,R33,R38,R39,R40 | 100R 0603 | CRCW0603100RFKEAC | 71-CRCW0603100RFKEAC | Mouser | 17 | 0.023 | 0.391
R8 | 1k2 0603 | ERJ-3RBD1201V | 667-ERJ-3RBD1201V | Mouser | 1 | 0.1 | 0.1
R27 | 2k 0603 | RR0816P-202-D | 754-RR0816P-202D | Mouser | 1 | 0.1 | 0.1
R1,R16,R17,R29,R30,R31,R5,R6,R7,R12,R14,R19, R4 | 10k 0603 | RR0816P-103-D | 754-RR0816P-103D | Mouser | 13 | 0.081 | 1.053
R2,R3,R11,R13 | 82k 0603 | RR0816P-823-D | 754-RR0816P-823D | Mouser | 4 | 0.1 | 0.4
R18 | 270k 0603 | RR0816P-274-D | 754-RR0816P-274D | Mouser | 1 | 0.1 | 0.1
J1 | DC-Jack | KLDX-0202-AC | 806-KLDX-0202-AC | Mouser | 1 | 0.44 | 0.44
J2,J3,J4,J5,J6 | RJ45-Buchse | 54601-908WPLF | 649-54601-908WPLF | Mouser | 5 | 0.54 | 2.7
C17,C21 | 120pF 0603 | C0603C121J5GAC | 80-C0603C121J5GAC | Mouser | 2 | 0.1 | 0.2
C11,C13,C12,C10,C6,C7,C8,C9,C31,C27,C28,C29,C30,C49,C50,C51,C52,C53,C54,C55,C56,C57,C58 | 100nF 0603 | 0603B104J500CT | 791-0603B104J500CT | Mouser | 23 | 0.108 | 2.484
C14,C15,C16,C19,C20,C18,C1,C2,C3,C4,C5,C22,C23,C24,C25,C26 | 10uF 1206 | 1206DD106MAT2A | 581-1206DD106MAT2A | Mouser | 16 | 0.209 | 3.344
LED1 | RGB-LED | PLCC-6 |  | selbst | 1 | 0 | 0
S1 | Taster | DIP-TASTER |  | selbst | 2 | 0 | 0
JP1 | NTC | NTC |  | selbst | 1 | 0 | 0
IC2 | Atmega88 | ATMEGA88PB-AU |  | selbst | 1 | 0 | 0
 |  |  |  |  |  |  | 42.512

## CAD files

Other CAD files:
doc/Messbox v3.f3d

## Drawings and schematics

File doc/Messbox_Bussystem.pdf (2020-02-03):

# Messkarte (STM32)

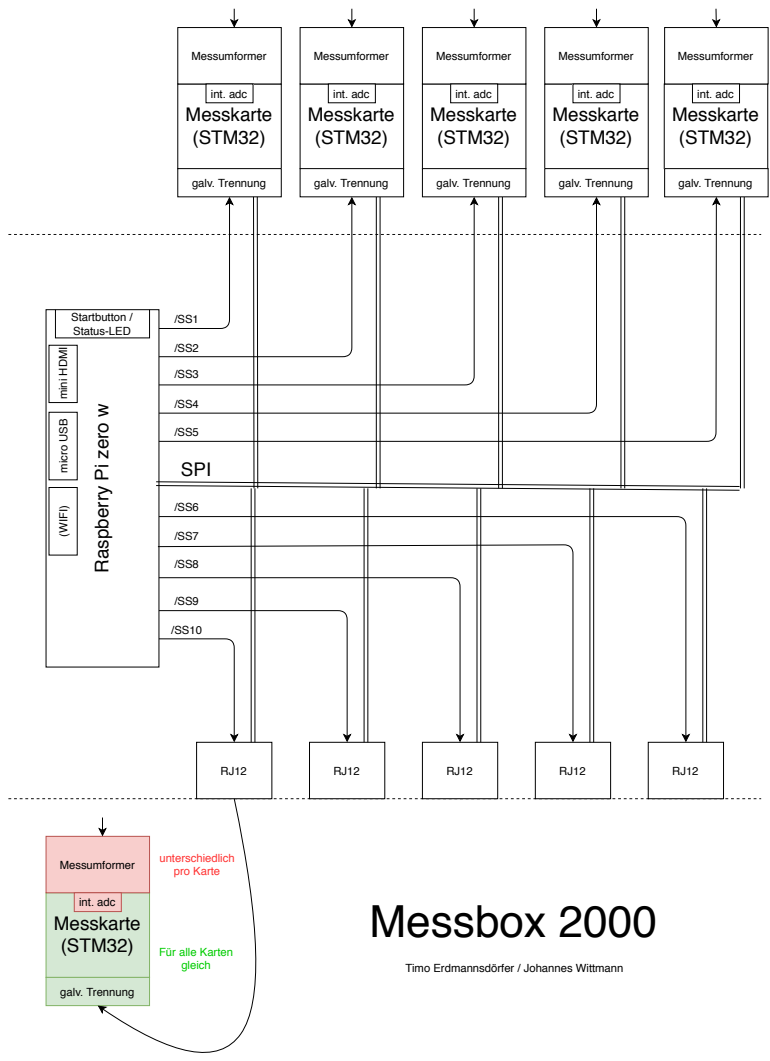
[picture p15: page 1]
Messkarte (STM32); galv. Trennung; Messumformer; int. adc; SPI; Startbutton / Status-LED; Messbox 2000; unterschiedlich pro Karte

mini HDMI micro USB (WIFI)

Raspberry Pi zero w

Für alle Karten
gleich

Timo Erdmannsdörfer / Johannes Wittmann

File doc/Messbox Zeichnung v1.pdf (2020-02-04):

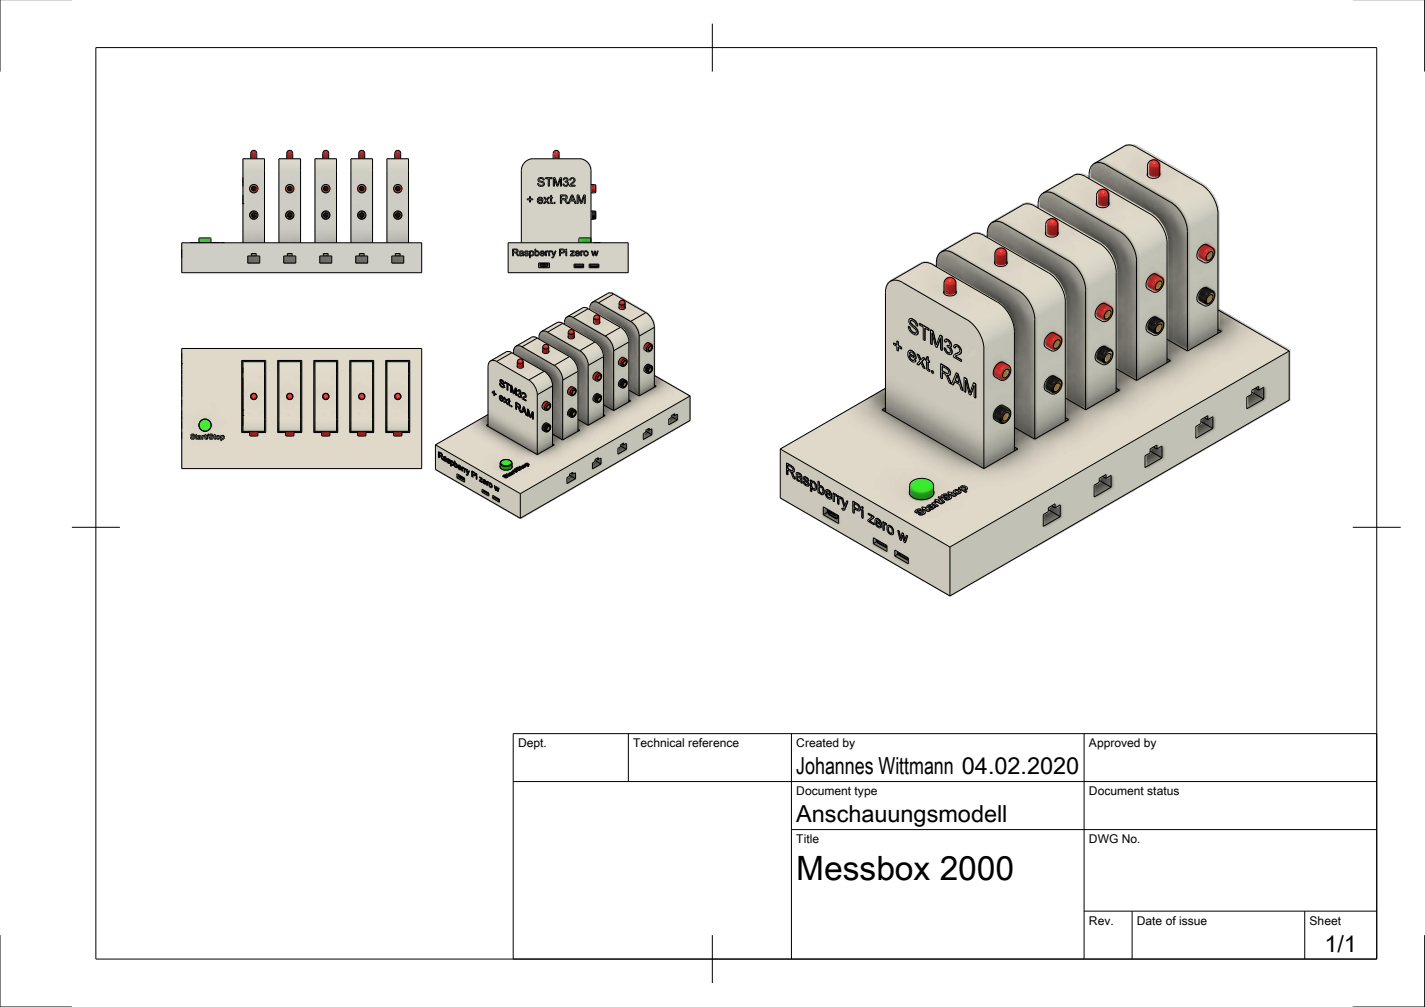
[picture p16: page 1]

Dept. | Technical reference | Created by Johannes Wittmann 04.02.2020 | Approved by

Document type Anschauungsmodell | Document status

Title Messbox 2000 | DWG No.

Rev. | Date of issue | Sheet 1/1

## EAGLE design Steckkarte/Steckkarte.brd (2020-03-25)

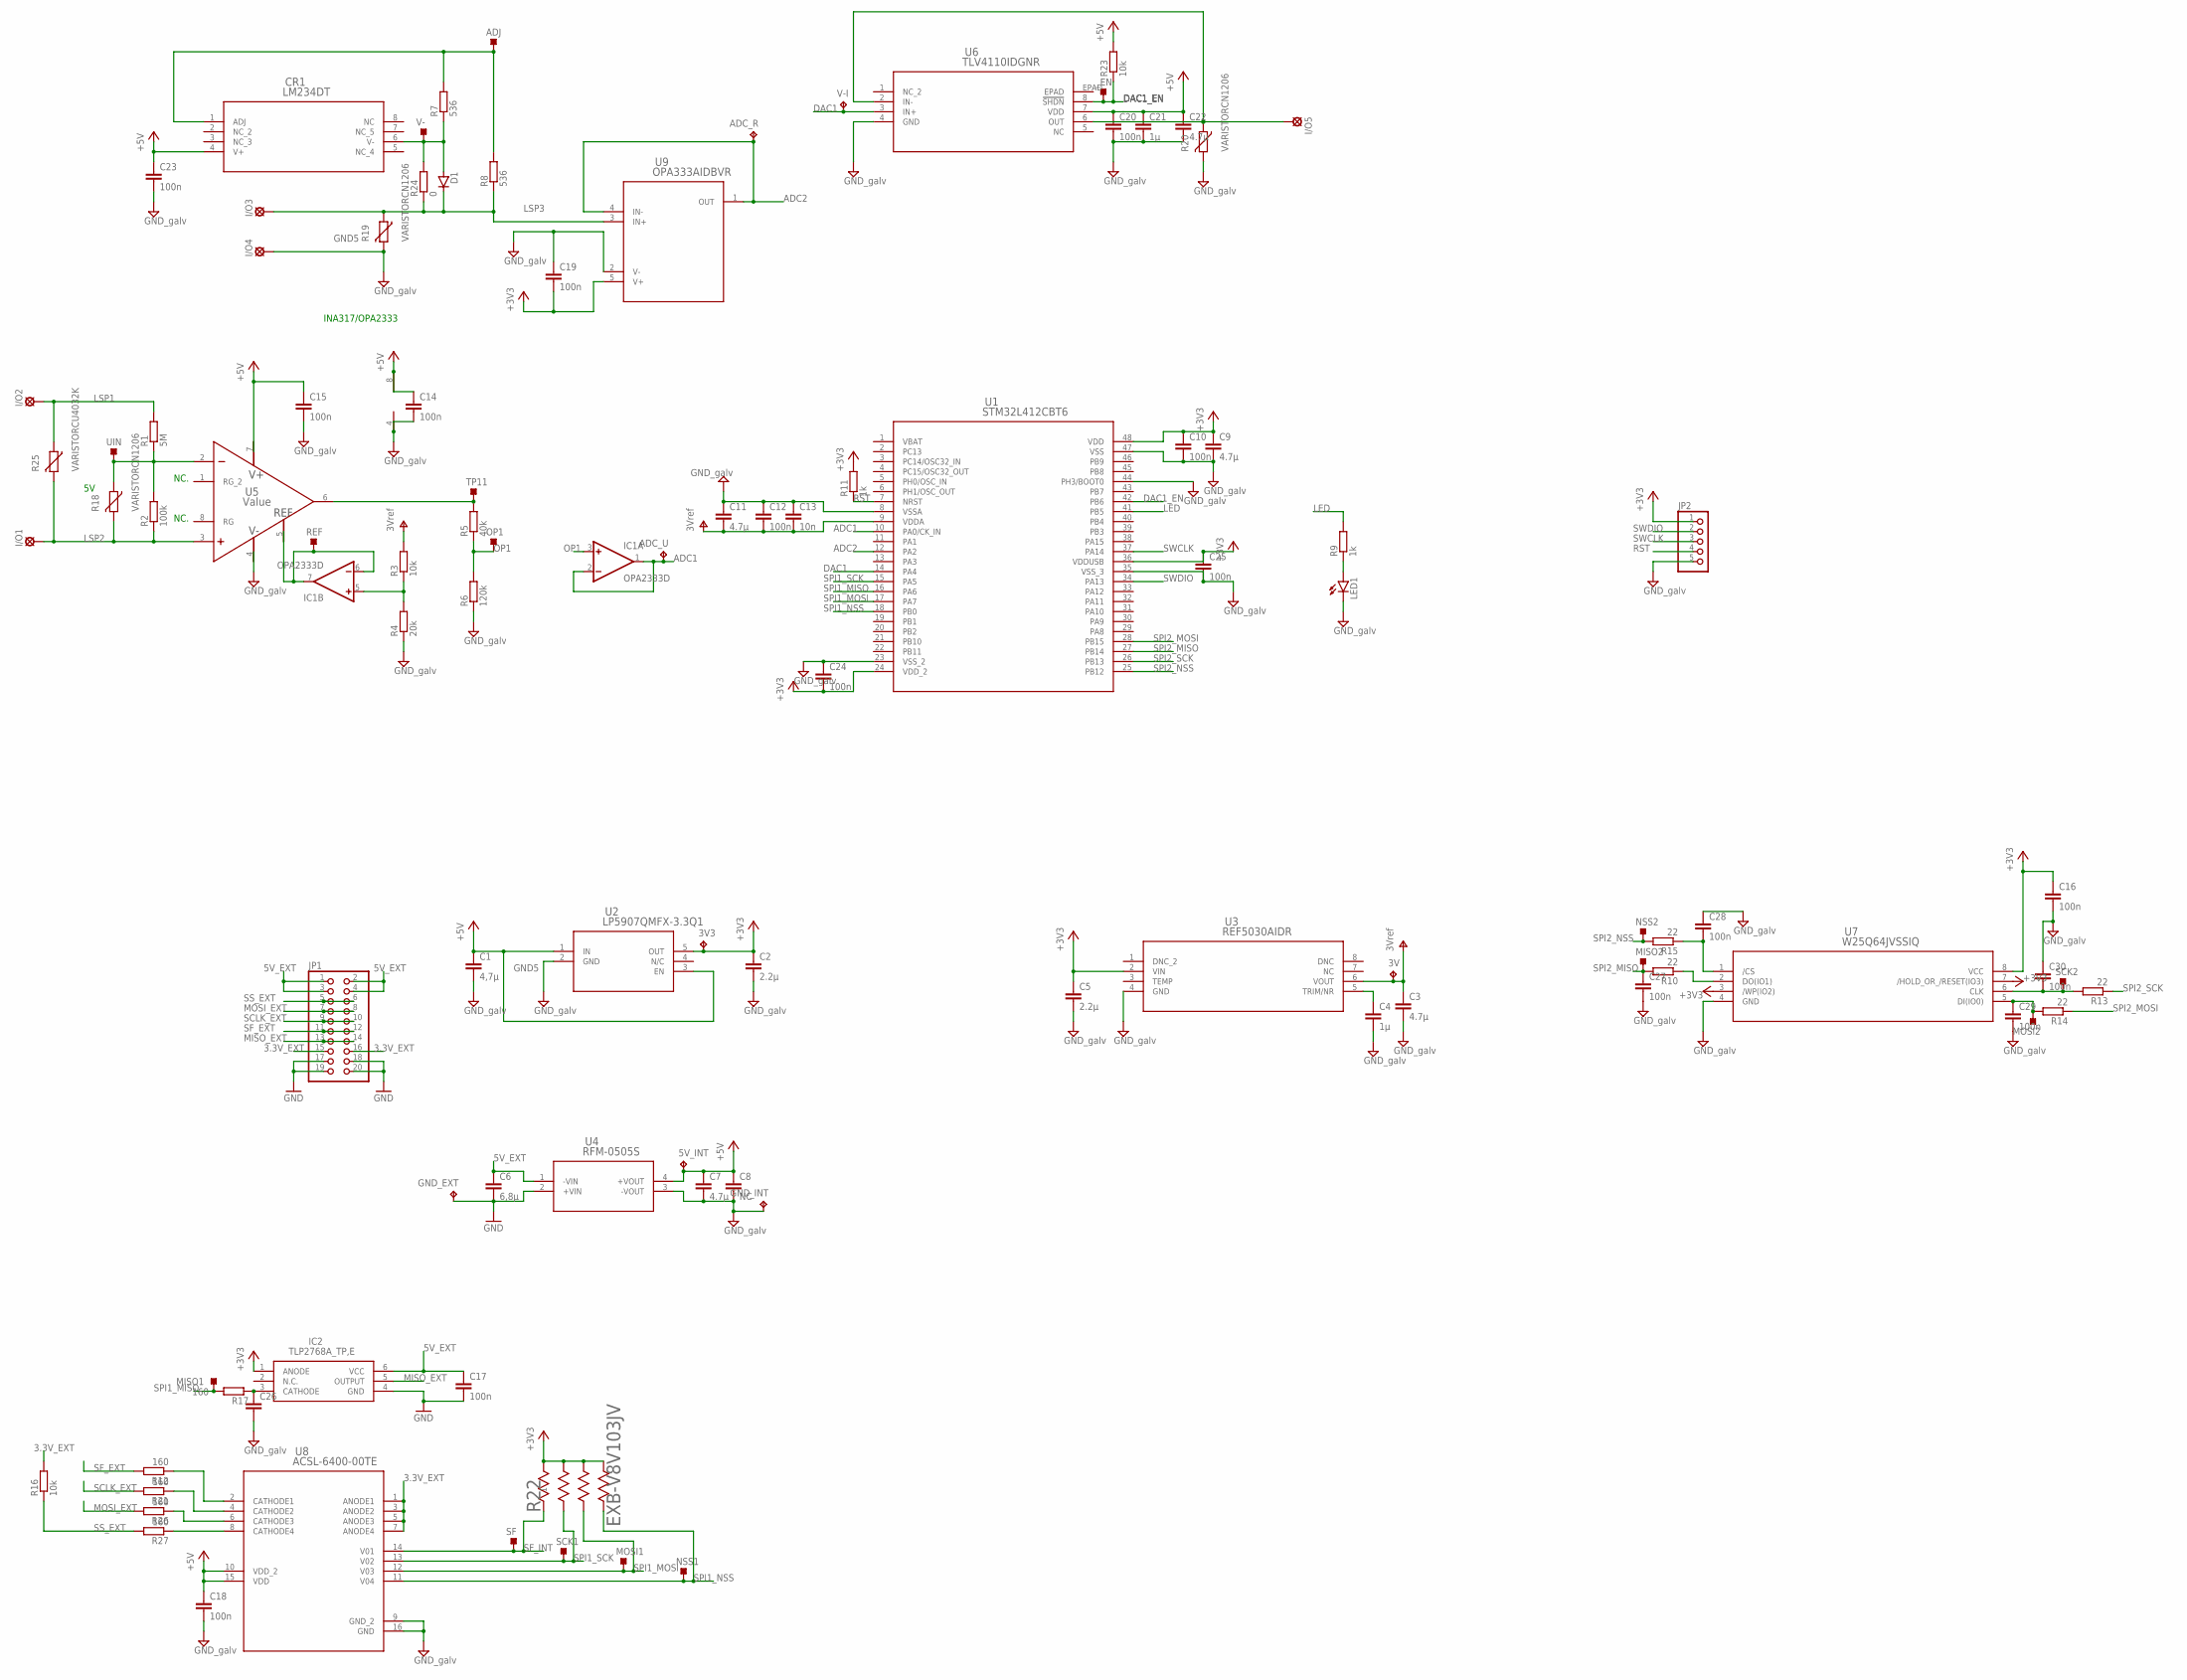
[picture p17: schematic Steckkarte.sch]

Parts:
3V, 3V3, 5V_INT: TPPAD1-13; P1-13
ADC_R: TPPAD1-13; P1-13
ADC_U: TPPAD1-13; P1-13
ADJ: TESTPOINT_TPS-SMD-10SN; TESTPOINT_SMD-10SN
C1: 4,7µ; C0603K
C2, C5: 2.2µ; C0603K
C3, C7, C9, C11, C22: 4.7µ; C0603K
C4, C21: 1µ; C0603K
C6: 6,8µ; C0603K
C8: NC; C0603K
C10, C12, C14, C15, C16, C17, C18, C19, C20, C23, C24, C25, C27, C28, C29, C30: 100n; C0603K
C13: 10n; C0603K
C26: C-EUC0603K; C0603K
CR1: LM234DT; SO-8
D1: D-SOD123; SOD123
GND_EXT: TPPAD1-13; P1-13
GND_INT: TPPAD1-13; P1-13
I/O1, I/O2, I/O3, I/O4, I/O5: SE14
IC1: OPA2333D; SO08
IC2: TLP2768A_TP,E; SOIC127P1000X220-6N
JP1: PINHD-2X10/90; 2X10/90
JP2: PINHD-1X5; 1X05
LED1: LED5MM
MISO1, MISO2: TESTPOINT_TPS-SMD-10SN; TESTPOINT_SMD-10SN
MOSI1, MOSI2: TESTPOINT_TPS-SMD-10SN; TESTPOINT_SMD-10SN
NSS1, NSS2: TESTPOINT_TPS-SMD-10SN; TESTPOINT_SMD-10SN
OP1: TESTPOINT_TPS-SMD-10SN; TESTPOINT_SMD-10SN
R1: 5M; R1206
R2: 100k; R1206
R3, R16, R23: 10k; R0603
R4: 20k; R0603
R5: 40k; R0603
R6: 120k; R0603
R7, R8: 536; R0603
R9, R11: 1k; R0603
R10, R13, R14, R15: 22; R0603
R12, R17, R21, R26, R27: 160; R0603
R18, R19, R20: VARISTORCN1206; CT/CN1206
R22: EXB-V8V103JV; EXBV8V
R24: 0; R0603
R25: VARISTORCU4032K; CU4032K
REF: TESTPOINT_TPS-SMD-10SN; TESTPOINT_SMD-10SN
SCK1, SCK2: TESTPOINT_TPS-SMD-10SN; TESTPOINT_SMD-10SN
SF: TESTPOINT_TPS-SMD-10SN; TESTPOINT_SMD-10SN
TP11: TESTPOINT_TPS-SMD-10SN; TESTPOINT_SMD-10SN
U1: STM32L412CBT6; LQFP-48
U2: LP5907QMFX-3.3Q1; DBV5
U3: REF5030AIDR; D8
U4: RFM-0505S
U5: Value; DGK0008A_N
U6: TLV4110IDGNR; DGN8_1P89X1P57
U7: W25Q64JVSSIQ; SOIC-8_5P28X5P28
U8: ACSL-6400-00TE; SOIC_6400-00TE
U9: OPA333AIDBVR; DBV5
UIN: TESTPOINT_TPS-SMD-10SN; TESTPOINT_SMD-10SN
V-: TESTPOINT_TPS-SMD-10SN; TESTPOINT_SMD-10SN
V-I: TPPAD1-13; P1-13
_EN: TESTPOINT_TPS-SMD-10SN; TESTPOINT_SMD-10SN

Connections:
3.3V_EXT: JP1.15, JP1.16, R16.2, U8.1 (ANODE1), U8.3 (ANODE2), U8.5 (ANODE3), U8.7 (ANODE4)
5V_EXT: C6.1, C17.1, IC2.6 (VCC), JP1.1, JP1.2, JP1.3, JP1.4, U4.1 (-VIN)
+3V3: 3V3.TP, C2.1, C5.1, C9.1, C10.1, C16.1, C19.2, C24.2, C25.1, IC2.1 (ANODE), JP2.1, R11.2, R22.5, R22.6, R22.7, R22.8, U1.24 (VDD_2), U1.36 (VDDUSB), U1.48 (VDD), U2.5 (OUT), U3.2 (VIN), U7.3 (/WP(IO2)), U7.7 (/HOLD_OR_/RESET(IO3)), U7.8 (VCC), U9.5 (V+)
+5V: 5V_INT.TP, C1.1, C7.1, C8.1, C14.1, C15.1, C18.1, C20.1, C21.1, C22.1, C23.1, CR1.4 (V+), IC1.8 (V+), R23.2, U2.1 (IN), U2.3 (EN), U4.4 (+VOUT), U5.7 (V+), U6.7 (VDD), U8.10 (VDD_2), U8.15 (VDD)
ADC1: ADC_U.TP, IC1.1 (OUT), IC1.2 (-IN), U1.10 (PA0/CK_IN)
ADC2: ADC_R.TP, U1.12 (PA2), U9.1 (OUT), U9.4 (IN-)
DAC1: U1.14 (PA4), U6.3 (IN+), V-I.TP
DAC1_EN: R23.1, U1.42 (PB6), U6.8 (!SHDN), _EN.TP
GND: C6.2, C17.2, GND_EXT.TP, IC2.4 (GND), JP1.17, JP1.18, JP1.19, JP1.20, U4.2 (+VIN)
GND5: C1.2, C2.2, C3.2, C4.2, C5.2, C7.2, C8.2, C9.2, C10.2, C11.1, C12.1, C13.1, C14.2, C15.2, C16.2, C18.2, C19.1, C20.2, C21.2, C22.2, C23.2, C24.1, C25.2, C26.2, C27.2, C28.1, C29.2, C30.1, GND_INT.TP, I/O4.MP, IC1.4 (V-), JP2.5, LED1.K (C), R4.1, R6.1, R19.2, R20.2, U1.8 (VSSA), U1.23 (VSS_2), U1.35 (VSS_3), U1.44 (PH3/BOOT0), U1.47 (VSS), U2.2 (GND), U3.4 (GND), U4.3 (-VOUT), U5.4 (V-), U6.4 (GND), U7.4 (GND), U8.9 (GND_2), U8.16 (GND), U9.2 (V-)
LED: R9.2, U1.41 (PB5)
LSP1: I/O2.MP, R1.2, R25.1
LSP2: I/O1.MP, R2.1, R18.2, R25.2, U5.3 (IN+)
LSP3: D1.1 (C), I/O3.MP, R8.1, R19.1, R24.1, U9.3 (IN+)
LSP5: I/O5.MP, R20.1, U6.2 (IN-), U6.6 (OUT)
MISO_EXT: IC2.5 (OUTPUT), JP1.13, JP1.14
MOSI_EXT: JP1.7, JP1.8, R26.2
unnamed: LED1.A, R9.1
unnamed: R1.1, R2.2, R18.1, U5.2 (IN-), UIN.TP
unnamed: R10.1, U7.2 (DO(IO1))
unnamed: R5.2, TP11.TP, U5.6 (OUT)
unnamed: IC1.5 (+IN), R3.1, R4.2
unnamed: C4.1, U3.5 (TRIM/NR)
unnamed: IC1.6 (-IN), IC1.7 (OUT), REF.TP, U5.5 (REF)
unnamed: R27.1, U8.8 (CATHODE4)
unnamed: CR1.6 (V-), D1.2 (A), R7.1, R24.2, V-.TP
unnamed: ADJ.TP, CR1.1 (ADJ), R7.2, R8.2
unnamed: C30.2, R13.2, SCK2.TP, U7.6 (CLK)
unnamed: C29.1, MOSI2.TP, R14.2, U7.5 (DI(IO0))
unnamed: C28.2, R15.1, U7.1 (/CS)
unnamed: R26.1, U8.6 (CATHODE3)
unnamed: R21.1, U8.4 (CATHODE2)
unnamed: R12.1, U8.2 (CATHODE1)
unnamed: C26.1, IC2.3 (CATHODE), R17.1
OP1: IC1.3 (+IN), OP1.TP, R5.1, R6.2
RST: JP2.4, R11.1, U1.7 (NRST)
SCLK_EXT: JP1.9, JP1.10, R21.2
SF_EXT: JP1.11, JP1.12, R12.2
SF_INT: R22.1, SF.TP, U8.14 (V01)
SPI1_MISO: MISO1.TP, R17.2, U1.16 (PA6)
SPI1_MOSI: MOSI1.TP, R22.3, U1.17 (PA7), U8.12 (V03)
SPI1_NSS: NSS1.TP, R22.4, U1.18 (PB0), U8.11 (V04)
SPI1_SCK: R22.2, SCK1.TP, U1.15 (PA5), U8.13 (V02)
SPI2_MISO: C27.1, MISO2.TP, R10.2, U1.27 (PB14)
SPI2_MOSI: R14.1, U1.28 (PB15)
SPI2_NSS: NSS2.TP, R15.2, U1.25 (PB12)
SPI2_SCK: R13.1, U1.26 (PB13)
SS_EXT: JP1.5, JP1.6, R16.1, R27.2
SWCLK: JP2.3, U1.37 (PA14)
SWDIO: JP2.2, U1.34 (PA13)
V+: 3V.TP, C3.1, C11.2, C12.2, C13.2, R3.2, U1.9 (VDDA), U3.6 (VOUT)
VBAT: U1.1 (VBAT)

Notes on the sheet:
NC.
INA317/OPA2333

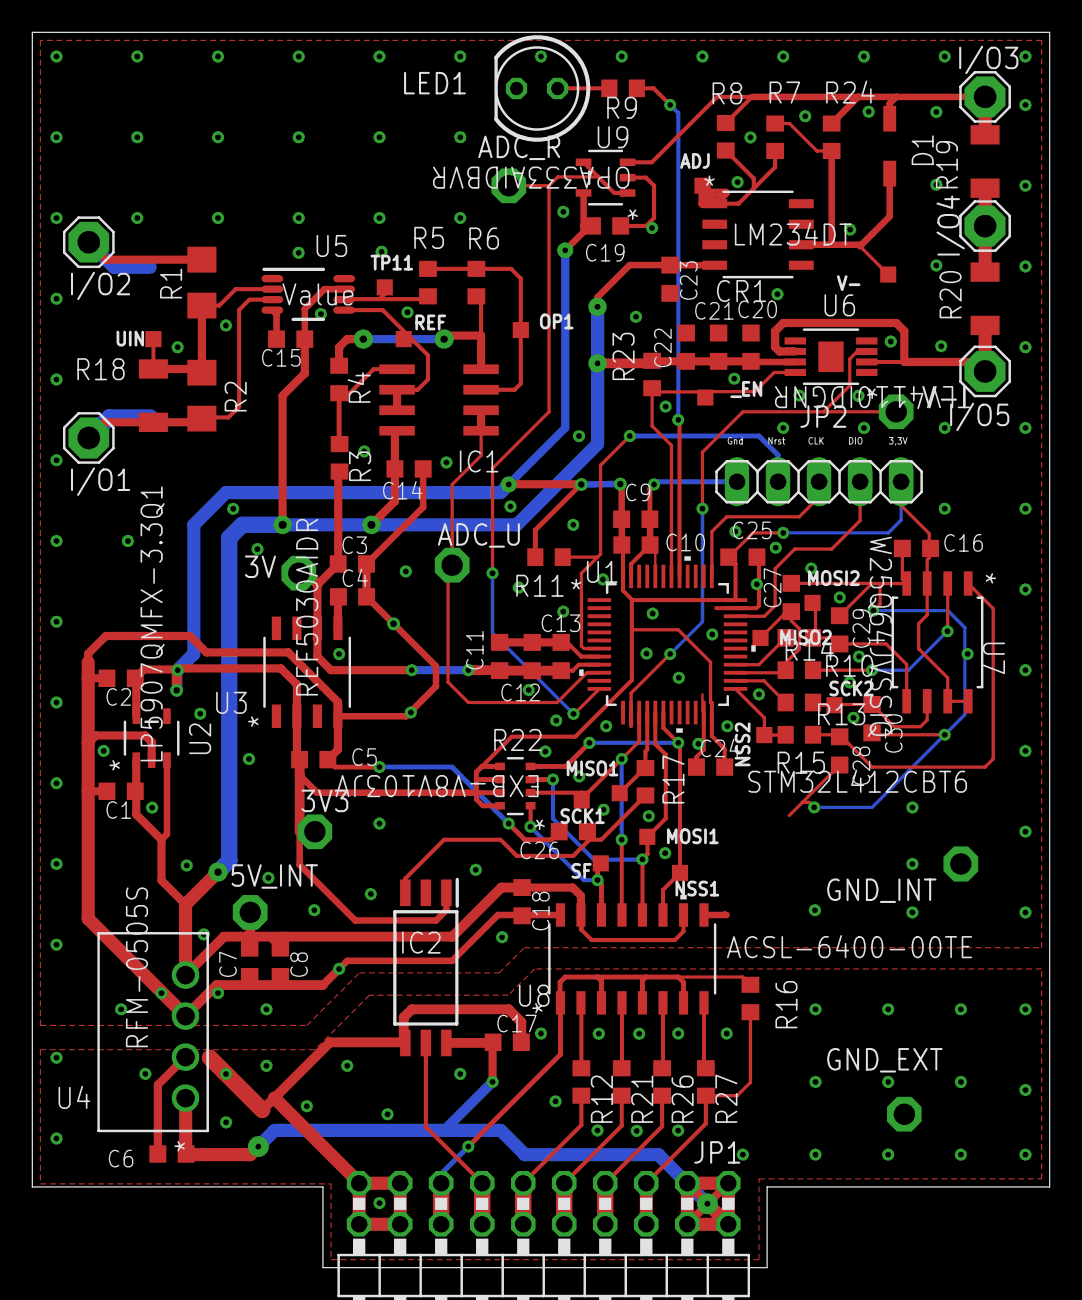
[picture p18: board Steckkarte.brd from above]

Board: 2 copper layers, 63.0 x 76.5 mm, 102 parts (1 on the bottom side), 51 nets.

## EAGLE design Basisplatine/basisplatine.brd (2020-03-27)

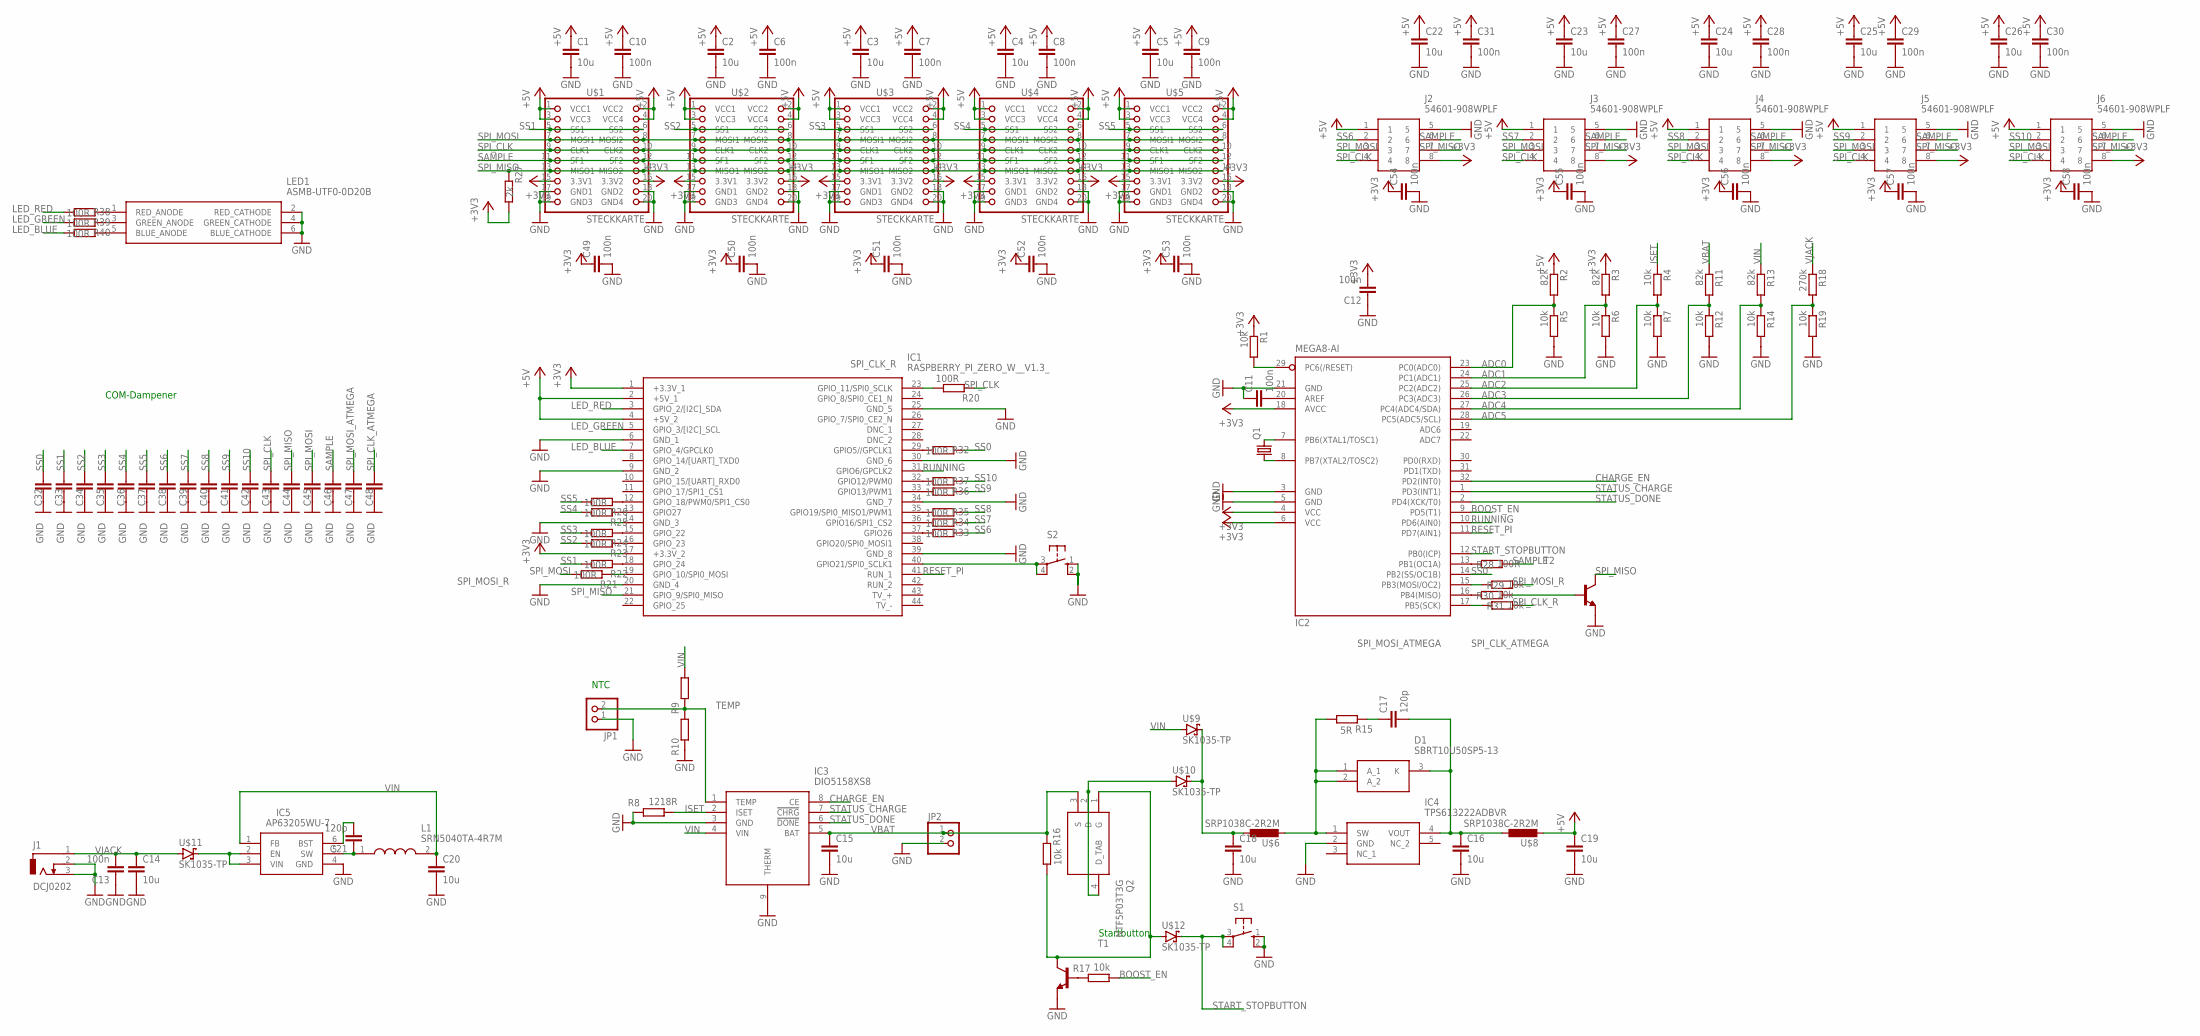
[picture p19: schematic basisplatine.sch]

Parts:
C1, C22: 10u; C1206
C2, C3, C4, C5, C14, C15, C16, C18, C19, C20, C23, C24, C25, C26: 10u; C1206K
C6, C7, C8, C9, C10, C11, C12, C13, C27, C28, C29, C30, C31, C49, C50, C51, C52, C53, C54, C55, C56, C57, C58: 100n; C0603K
C17, C21: 120p; C0603K
C32, C33, C34, C35, C36, C37, C38, C39, C40, C41, C42, C43, C44, C45, C46, C47, C48: C-EUC0603K; C0603K
D1: SBRT10U50SP5-13; SBRT10U50SP513
IC1: RASPBERRY_PI_ZERO_W__V1.3_; RASPBERRYPIZEROWV13
IC2: MEGA8-AI; TQFP32-08
IC3: DIO5158XS8; SOIC127P600X170-9N
IC4: TPS613222ADBVR; SOT95P280X145-5N
IC5: AP63205WU-7; SOT95P280X100-6N
J1: DCJ0202
J2, J3, J4, J5, J6: 54601-908WPLF; 54601908WPLF
JP1, JP2: PINHD-1X2; 1X02
L1: SRN5040TA-4R7M; SRN5040TA4R7M
LED1: ASMB-UTF0-0D20B; ASMBUTF00D20B
Q1: CRYSTALTC38H; TC38H
Q2: NTF5P03T3G; SOT230P700X175-4N
R1, R4, R5, R6, R7, R12, R14, R16, R17, R19, R29, R30, R31: 10k; R0603
R2, R3, R11, R13: 82k; R0603
R8: 1218R; R0603
R9, R10: R-EU_R0603; R0603
R15: 5R; R0603
R18: 270k; R0603
R20, R21, R22, R23, R24, R25, R26, R28, R32, R33, R34, R35, R36, R37, R38, R39, R40: 100R; R0603
R27: 2k; R0603
S1, S2: 10-XX; B3F-10XX
T1, T2: BC808-NPN-SOT23-BEC; SOT23-BEC
U$1, U$2, U$3, U$4, U$5: STECKKARTE; 2X10
U$6, U$8: SRP1038C-2R2M
U$9, U$10, U$11, U$12: SK1035-TP; INDC2520X120N

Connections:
+3V3: C12.2, C49.1, C50.1, C51.1, C52.1, C53.1, C54.1, C55.1, C56.1, C57.1, C58.1, IC1.1 (+3.3V_1), IC1.17 (+3.3V_2), IC2.4 (VCC), IC2.6 (VCC), IC2.18 (AVCC), J2.8, J3.8, J4.8, J5.8, J6.8, R1.1, R3.1, R27.2, U$1.15 (3.3V1), U$1.16 (3.3V2), U$2.15 (3.3V1), U$2.16 (3.3V2), U$3.15 (3.3V1), U$3.16 (3.3V2), U$4.15 (3.3V1), U$4.16 (3.3V2), U$5.15 (3.3V1), U$5.16 (3.3V2)
+5V: C1.1, C2.1, C3.1, C4.1, C5.1, C6.1, C7.1, C8.1, C9.1, C10.1, C19.1, C22.1, C23.1, C24.1, C25.1, C26.1, C27.1, C28.1, C29.1, C30.1, C31.1, IC1.2 (+5V_1), IC1.4 (+5V_2), J2.1, J3.1, J4.1, J5.1, J6.1, R2.1, U$1.1 (VCC1), U$1.2 (VCC2), U$1.3 (VCC3), U$1.4 (VCC4), U$2.1 (VCC1), U$2.2 (VCC2), U$2.3 (VCC3), U$2.4 (VCC4), U$3.1 (VCC1), U$3.2 (VCC2), U$3.3 (VCC3), U$3.4 (VCC4), U$4.1 (VCC1), U$4.2 (VCC2), U$4.3 (VCC3), U$4.4 (VCC4), U$5.1 (VCC1), U$5.2 (VCC2), U$5.3 (VCC3), U$5.4 (VCC4), U$8.P$2 (2)
ADC0: IC2.23 (PC0(ADC0)), R2.2, R5.1
ADC1: IC2.24 (PC1(ADC1)), R3.2, R6.1
ADC2: IC2.25 (PC2(ADC2)), R4.2, R7.1
ADC3: IC2.26 (PC3(ADC3)), R11.2, R12.1
ADC4: IC2.27 (PC4(ADC4/SDA)), R13.2, R14.1
ADC5: IC2.28 (PC5(ADC5/SCL)), R18.2, R19.1
BOOST_EN: IC2.9 (PD5(T1)), R17.2
CHARGE_EN: IC2.32 (PD2(INT0)), IC3.8 (CE)
CLOCK_EN: IC2.29 (PC6(/RESET)), R1.2
GND: C1.2, C2.2, C3.2, C4.2, C5.2, C6.2, C7.2, C8.2, C9.2, C10.2, C11.1, C12.1, C13.1, C14.2, C15.2, C16.2, C18.2, C19.2, C20.2, C22.2, C23.2, C24.2, C25.2, C26.2, C27.2, C28.2, C29.2, C30.2, C31.2, C32.1, C33.1, C34.1, C35.1, C36.1, C37.1, C38.1, C39.1, C40.1, C41.1, C42.1, C43.1, C44.1, C45.1, C46.1, C47.1, C48.1, C49.2, C50.2, C51.2, C52.2, C53.2, C54.2, C55.2, C56.2, C57.2, C58.2, IC1.6 (GND_1), IC1.9 (GND_2), IC1.14 (GND_3), IC1.20 (GND_4), IC1.25 (GND_5), IC1.30 (GND_6), IC1.34 (GND_7), IC1.39 (GND_8), IC2.3 (GND), IC2.5 (GND), IC2.21 (GND), IC3.3 (GND), IC3.9 (THERM), IC4.2 (GND), IC5.4 (GND), J1.2, J1.3, J2.5, J3.5, J4.5, J5.5, J6.5, JP1.1, JP2.2, LED1.2 (RED_CATHODE), LED1.4 (GREEN_CATHODE), LED1.6 (BLUE_CATHODE), R5.2, R6.2, R7.2, R8.1, R10.1, R12.2, R14.2, R19.2, S1.1 (S), S1.2 (S1), S2.1 (S), S2.2 (S1), T1.E, T2.E, U$1.17 (GND1), U$1.18 (GND2), U$1.19 (GND3), U$1.20 (GND4), U$2.17 (GND1), U$2.18 (GND2), U$2.19 (GND3), U$2.20 (GND4), U$3.17 (GND1), U$3.18 (GND2), U$3.19 (GND3), U$3.20 (GND4), U$4.17 (GND1), U$4.18 (GND2), U$4.19 (GND3), U$4.20 (GND4), U$5.17 (GND1), U$5.18 (GND2), U$5.19 (GND3), U$5.20 (GND4)
ISET: IC3.2 (ISET), R4.1, R8.2
LED_BLUE: IC1.7 (GPIO_4/GPCLK0), R40.2
LED_GREEN: IC1.5 (GPIO_3/[I2C]_SCL), R39.2
LED_RED: IC1.3 (GPIO_2/[I2C]_SDA), R38.2
unnamed: D1.1 (A_1), D1.2 (A_2), IC4.1 (SW), R15.2, U$6.P$2 (2)
unnamed: C11.2, IC2.20 (AREF)
unnamed: IC2.7 (PB6(XTAL1/TOSC1)), Q1.2
unnamed: IC2.8 (PB7(XTAL2/TOSC2)), Q1.1
unnamed: IC5.2 (EN), IC5.3 (VIN), U$11.2 (C)
unnamed: C21.1, IC5.5 (SW), L1.1
unnamed: C17.1, R15.1
unnamed: C16.1, C17.2, D1.3 (K), IC4.4 (VOUT), U$8.P$1 (1)
unnamed: C18.1, U$6.P$1 (1), U$9.2 (C), U$10.2 (C)
unnamed: R17.1, T1.B
unnamed: Q2.2 (D), Q2.4 (D_TAB), U$10.1 (A)
unnamed: C21.2, IC5.6 (BST)
unnamed: R30.2, T2.B
unnamed: IC1.18 (GPIO_24), R22.1
unnamed: IC1.16 (GPIO_23), R23.1
unnamed: IC1.15 (GPIO_22), R24.1
unnamed: IC1.13 (GPIO27), R25.1
unnamed: IC1.12 (GPIO_18/PWM0/SPI1_CS0), R26.1
unnamed: IC2.13 (PB1(OC1A)), R28.1
unnamed: IC1.40 (GPIO21/SPI0_SCLK1), S2.3, S2.4 (P1)
unnamed: IC2.16 (PB4(MISO)), R30.1
unnamed: Q2.1 (G), R16.2, T1.C, U$12.1 (A)
unnamed: IC1.29 (GPIO5//GPCLK1), R32.2
unnamed: IC1.32 (GPIO12/PWM0), R37.2
unnamed: IC1.33 (GPIO13/PWM1), R36.2
unnamed: IC1.35 (GPIO19/SPI0_MISO1/PWM1), R35.2
unnamed: IC1.36 (GPIO16/SPI1_CS2), R34.2
unnamed: IC1.37 (GPIO26), R33.2
unnamed: LED1.1 (RED_ANODE), R38.1
unnamed: LED1.3 (GREEN_ANODE), R39.1
unnamed: LED1.5 (BLUE_ANODE), R40.1
RESET_PI: IC1.41 (RUN_1), IC2.11 (PD7(AIN1))
RUNNING: IC1.31 (GPIO6/GPCLK2), IC2.10 (PD6(AIN0))
SAMPLE: C46.2, J2.6, J3.6, J4.6, J5.6, J6.6, R28.2, U$1.11 (SF1), U$1.12 (SF2), U$2.11 (SF1), U$2.12 (SF2), U$3.11 (SF1), U$3.12 (SF2), U$4.11 (SF1), U$4.12 (SF2), U$5.11 (SF1), U$5.12 (SF2)
SPI_CLK: C43.2, J2.4, J3.4, J4.4, J5.4, J6.4, R20.1, U$1.9 (CLK1), U$1.10 (CLK2), U$2.9 (CLK1), U$2.10 (CLK2), U$3.9 (CLK1), U$3.10 (CLK2), U$4.9 (CLK1), U$4.10 (CLK2), U$5.9 (CLK1), U$5.10 (CLK2)
SPI_CLK_ATMEGA: C48.2, IC2.17 (PB5(SCK)), R31.1
SPI_CLK_R: IC1.23 (GPIO_11/SPI0_SCLK), R20.2, R31.2
SPI_MISO: C44.2, IC1.21 (GPIO_9/SPI0_MISO), J2.7, J3.7, J4.7, J5.7, J6.7, R27.1, T2.C, U$1.13 (MISO1), U$1.14 (MISO2), U$2.13 (MISO1), U$2.14 (MISO2), U$3.13 (MISO1), U$3.14 (MISO2), U$4.13 (MISO1), U$4.14 (MISO2), U$5.13 (MISO1), U$5.14 (MISO2)
SPI_MOSI: C45.2, J2.3, J3.3, J4.3, J5.3, J6.3, R21.2, U$1.7 (MOSI1), U$1.8 (MOSI2), U$2.7 (MOSI1), U$2.8 (MOSI2), U$3.7 (MOSI1), U$3.8 (MOSI2), U$4.7 (MOSI1), U$4.8 (MOSI2), U$5.7 (MOSI1), U$5.8 (MOSI2)
SPI_MOSI_ATMEGA: C47.2, IC2.15 (PB3(MOSI/OC2)), R29.1
SPI_MOSI_R: IC1.19 (GPIO_10/SPI0_MOSI), R21.1, R29.2
SS0: C32.2, IC2.14 (PB2(SS/OC1B)), R32.1
SS1: C33.2, R22.2, U$1.5 (SS1), U$1.6 (SS2)
SS2: C34.2, R23.2, U$2.5 (SS1), U$2.6 (SS2)
SS3: C35.2, R24.2, U$3.5 (SS1), U$3.6 (SS2)
SS4: C36.2, R25.2, U$4.5 (SS1), U$4.6 (SS2)
SS5: C37.2, R26.2, U$5.5 (SS1), U$5.6 (SS2)
SS6: C38.2, J2.2, R33.1
SS7: C39.2, J3.2, R34.1
SS8: C40.2, J4.2, R35.1
SS9: C41.2, J5.2, R36.1
SS10: C42.2, J6.2, R37.1
START_STOPBUTTON: IC2.12 (PB0(ICP)), S1.3, S1.4 (P1), U$12.2 (C)
STATUS_CHARGE: IC2.1 (PD3(INT1)), IC3.7 (!CHRG)
STATUS_DONE: IC2.2 (PD4(XCK/T0)), IC3.6 (!DONE)
TEMP: IC3.1 (TEMP), JP1.2, R9.1, R10.2
VBAT: C15.1, IC3.5 (BAT), JP2.1, Q2.3 (S), R11.1, R16.1
VIN: C20.1, IC3.4 (VIN), IC5.1 (FB), L1.2, R9.2, R13.1, U$9.1 (A)
VJACK: C13.2, C14.1, J1.1, R18.1, U$11.1 (A)

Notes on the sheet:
NTC
Startbutton
COM-Dampener

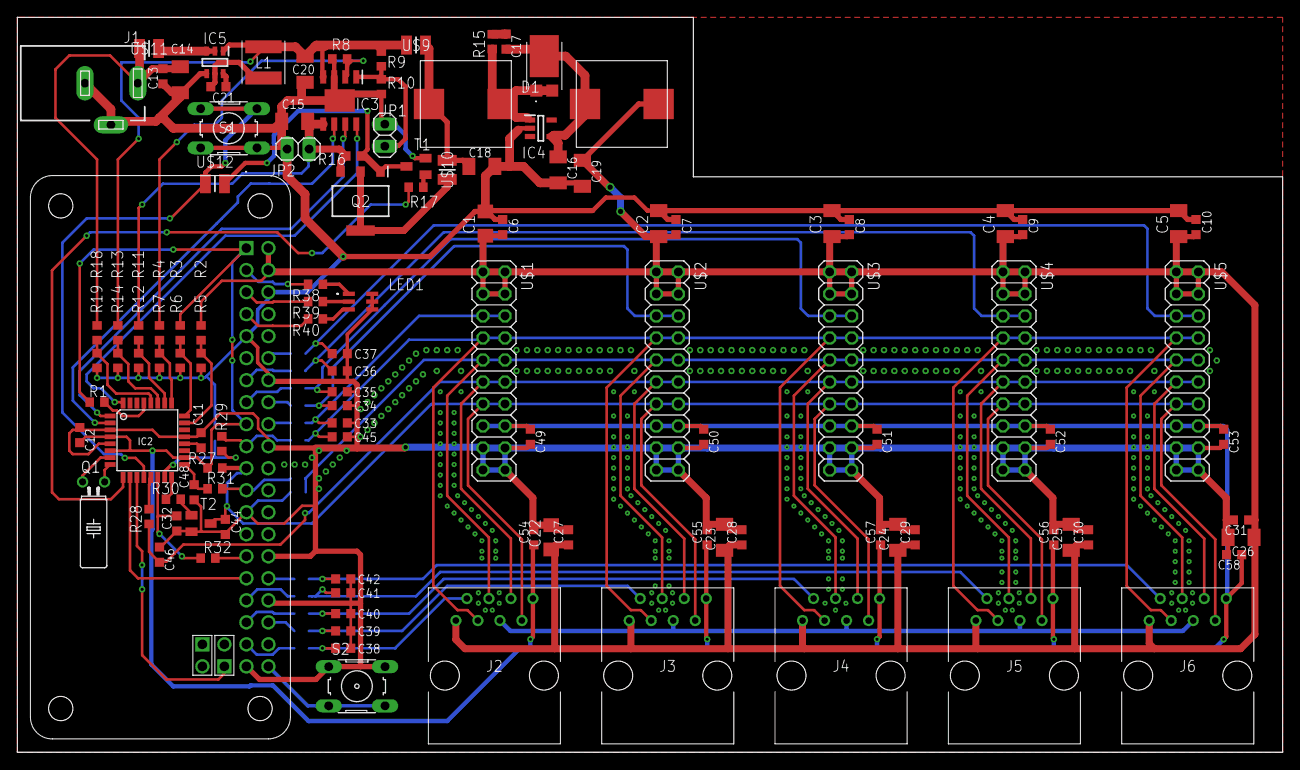
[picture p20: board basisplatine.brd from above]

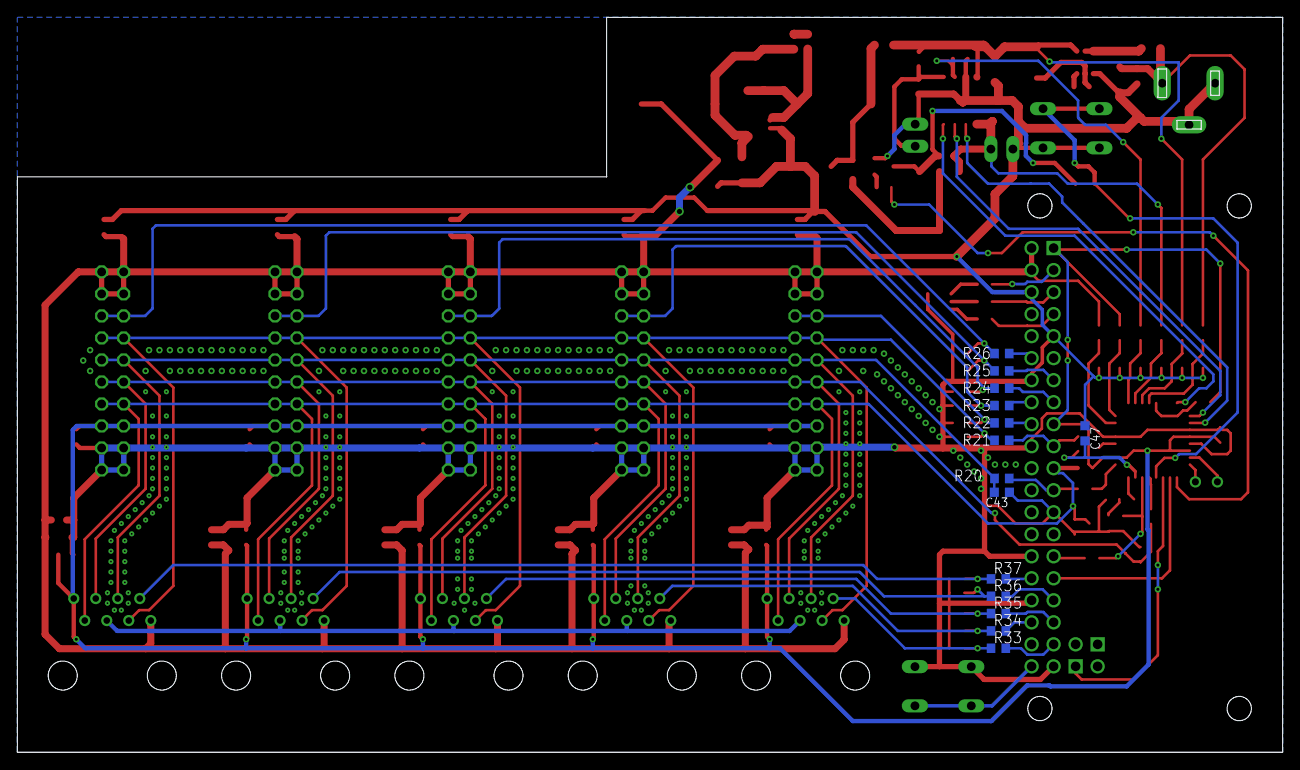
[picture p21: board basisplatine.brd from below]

Board: 2 copper layers, 146.0 x 84.8 mm, 131 parts (14 on the bottom side), 75 nets.

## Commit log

2020-02-04 Added 3d-model (or modell)
    [Messbox v3.f3d]
2020-02-06 Setup Steckkarten project and added Raspberry UML
    [SPI-Protokoll.xlsx]
2020-02-07 reworked SPI commands
    [SPI-Protokoll.xlsx]
2020-02-11 startet Raspberry Pi GUI
2020-02-17 Added Parameters
    [SPI-Protokoll.xlsx]
2020-02-18 Minor changes
    [SPI-Protokoll.xlsx]
2020-02-19 liste bauelemente
    [Liste_Bauelemente.xlsx]
2020-02-29 Added Control thread and Karte Destructor
2020-03-05 Basisplatine: Raspberry Pi, Samplefrequenz, Steckkarten
    [basisplatine.brd, basisplatine.sch]
2020-03-14 added battery managment
    [basisplatine.brd, basisplatine.sch]
2020-03-15 Added dampening Cs on SPI and RJ45
    [basisplatine.brd, basisplatine.sch]
2020-03-18 Added SPI-decoder
    [SPI-Protokoll.xlsx]
2020-03-20 Added Stueckliste, Taster, LED
    [Stueckliste.xlsx, basisplatine.brd, basisplatine.sch]
2020-03-20 eagel layout
    [Steckkarte.brd, Steckkarte.sch, copper_bottom.gbr, copper_top.gbr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]
2020-03-20 update layout
    [Steckkarte.brd, Steckkarte.sch, copper_bottom.gbr, copper_top.gbr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]
2020-03-20 Fixed some stuff
    [Steckkarte.brd, Steckkarte.sch]
2020-03-21 Added 3,3V and vias to Basisplatine, ...
    [Stueckliste.xlsx, basisplatine.brd, basisplatine.sch]
2020-03-24 Added parameter-decoder to raspberry
    [SPI-Protokoll.xlsx]
2020-03-24 Added rest of protokoll in post
    [SPI-Protokoll.xlsx]
2020-03-24 steckkarte die 2.te
    [Bestellung_Steckarte.xlsx, Steckkarte.brd, Steckkarte.sch, copper_bottom.gbr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]
2020-03-25 Refactored fake SPI, add get_daten, get_status, draw graph in qt thread
    [SPI-Protokoll.xlsx]
2020-03-27 Added cam for Basisplatine / Bestelldaten
    [Stueckliste.xlsx, Stückliste-Messbox.xlsx, basisplatine.brd]
2020-03-31 Changed to little endian-com; Enhanced timescale at higher numbers by changing to double in chart, Added get_status
    [SPI-Protokoll.xlsx, copper_bottom.gbr, copper_top.gbr, drills.xln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]
2020-05-13 Started software for atmega88 (sample freq)
2020-07-13 Updated spi protocoll; added dummy module
    [SPI-Protokoll.xlsx]
2020-07-16 Added DMA for data transferer, changed spi protokol
    [SPI-Protokoll.xlsx]
2020-07-17 fixed some things
    [SPI-Protokoll.xlsx]
2020-07-18 Added synchronized Sample Frequency and fixed priority in Steckkarte_moc
2020-08-09 converted Steckkarte_moc to STM32L431CBTx
2020-08-25 Added multiple ADC channels; smal adc input filter
2020-08-29 Restructured drictory structure
    [Bestellung_Steckarte.xlsx, Steckkarte.brd, Steckkarte.sch, Stückliste-Messbox.xlsx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]
2020-08-31 added simple UML for various parts of Raspberry
2020-09-12 switched from wiringpi to bcm2835 library

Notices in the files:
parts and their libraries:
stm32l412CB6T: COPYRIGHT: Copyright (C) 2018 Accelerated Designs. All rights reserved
